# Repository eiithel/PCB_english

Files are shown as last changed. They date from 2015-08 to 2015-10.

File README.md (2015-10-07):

#**Introduction**  
There is currently no cure for autism. Special educators often struggle to communicate with children
sometimes immured in their silence. Autistic children can develop their language and facilitate their
interpersonal interactions with the help of early childhood management and special education.   
According to recent studies, the robot is a relevant tool for reducing some autistic symptoms, such as
joint attention deficit disorder. It also promotes generalization of skills.   
I proposed a new hardware and software architecture for Leka's first educational robot, as an extension
to its control system. This new architecture is based on a Linux kernel.   
This expansion provides support for experimentation and verification of embedded Linux applications
for a robotic base.    
**Key words**: robotics, autism, hardware conception, embedded linux

##**Functional requirements**

This card has been developed for the purpose of writing code at rapid speeds. It isn't the final version of Moti but it will be rather useful for developers, helping them to realize their tests and to validate this type of architecture. The card allows connection between `actuators` that permits the robot to live and to move and there are also `sensors` that permit the robot to be aware of its environment and to react consequential to that environment.

* Actuators
  * Motor control
  * RGB LEDs control
*  Datas/Sensoring
  *  Accelerometer/gyroscope
  *  Microphone

_the video is not supported in this version._

##**Components choice**

###Control part

* **Teensy 3.1**  



The control card is equipped with a __Teensy__ ARM Cortex 32 bits, a powerfull 32 bits MCU.   
This module is suitable for `C/C++` programming and is compatible with code written for __Arduino__. It is also featured with a large number of IO pinouts (_total of 34_). The Teensy is dedicated to three tasks :

*  Communicate to the __Arietta__ informations concerning the differents modules/sensors and to manage the different requests.
* To deploy 12 GPIO and one serial port.
* To Manage enslavement motor calculations.

>The code written on this card doesn't have to be modified. It should have just the simpliest code possible.
.

   * **Arietta**  
  

The __Arietta__ is a little embedded linux system based on a very swift ARM9. (_400MHZ_) it is equipped with a WIFI module, several GPIOs and a serial port connected to the __Teensy__. This comprises the central intelligence of the robot and is dedicated to several tasks :

  * To receive and to send information and requests to the __Teensy__.
  * To manage all Moti's intelligence. (_This part can be developped on a computer before being embedded on the card_).
  * Web server in order to develop applications permitting a certain number of clients to use its services (_Smartphones and tablets_).

>An Arietta's i2C bus is available on the card to add eventual sensor.   

A simple example of how to communicate beetween Arietta and Teensy :  
<https://github.com/eiithel/node_Serial>   
I used NodeJS for my tests.

###Motors

Motors are controlled by the control card but they need a dedicated integrated circuit to supply them enough power in order to run correctly. This is what permits the POLULU module based on a __TB6612FNG__ chip.

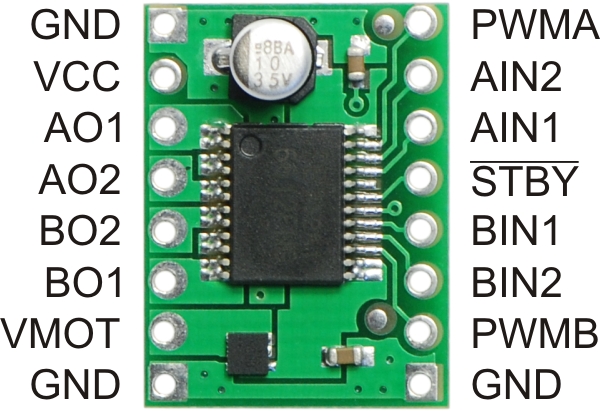
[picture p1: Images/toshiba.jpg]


PWMs and logic (AIN, BIN) are provided by the **Teensy**.

You can see a use case here: <https://github.com/eiithel/motors_test>    

>Be carefull. The **Teensy** is provided by 3 Timers.  
Motors PWMs come from **Timer0** but this timer is already used for **GSCLK** and **SIN** signals of the **TLC** due to pin sharing.  
You have to replace this PWMs by Outputs provided by Timer2 which is not used.  
This Timer is located under the **Teensy** (_pins 25 & 32_).

### **RGB LEDs**

In order to pilot 6 RGB LEDs, we need 6*3 = 18 channels. It is out of the question to use all the PWM Teensy outputs for that. The trick is to use a LED's driver that will allow us to increase our number of avalaible PWM outputs. This driver is controlled by the i2C Bus and provids 16 PWM channels. The 2 missing channels will be provided by the Teensy itself. The used component is the __TLC5940__ (Texas Instrument).



You can see a use case here: <https://github.com/eiithel/TLC4950_test>

##**Supplies**

The robot is designed with separate voltage regulators for digital and analog supply.   
The control part of the architecture needs to be supplied by 5V. The motor and its components need 6V. The solution was to use DC/DC adjustable regulators in order to provide good tensions scales.

**PTN78000WAH** _(Texas Instrument)_



This component can supply a max output current of 3A which is enough to run motors. It works for a 7 to 36V wide input tension. It permits to obtain a 2.5 to 22V wide output regulate tension. The output voltage is set using a single external resistor.

* 21 kohm for `5V`
* 13 kohm for `6V`
 
>All the passive components of the circuit are _SMD_ in order to save space on the board.

__BE CAREFULL__

This input is not protected against over and reverse voltages.  
When supplying the board take care to not invert anode and cathode. It would cause irreversible damages to the whole board.

###**A little display of the card**

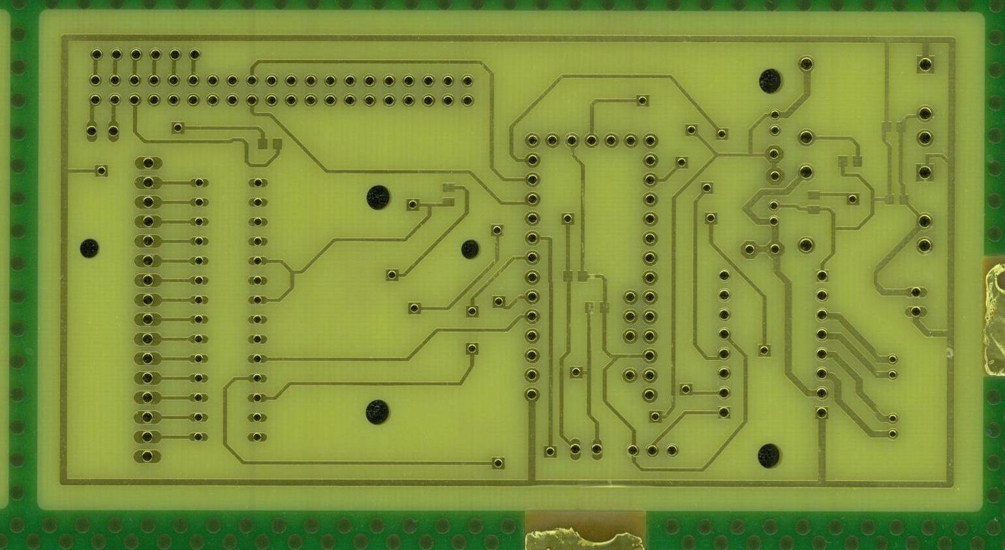
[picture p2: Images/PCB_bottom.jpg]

> <center>_Bottom face_</center>

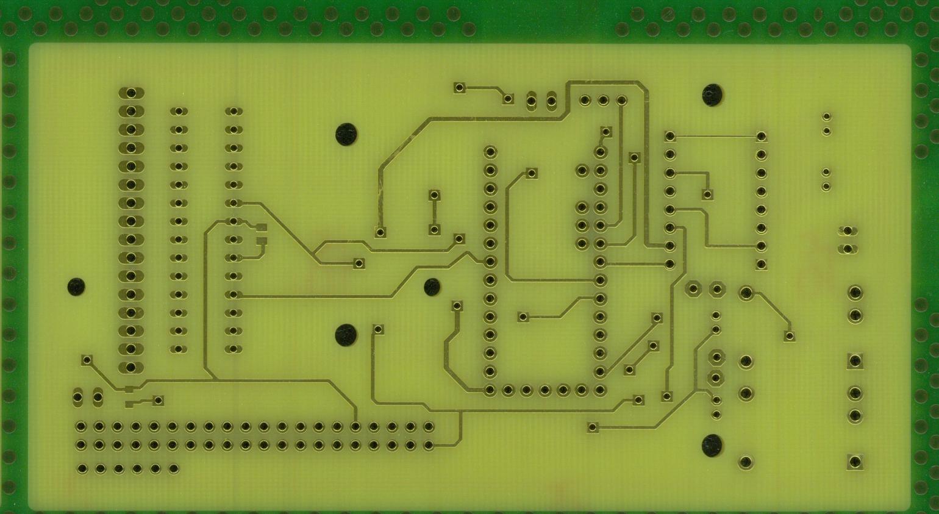
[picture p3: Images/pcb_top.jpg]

><center>_Top face_</center>

###__Bloc diagram__

To sum up, here is the electronical architecture of the prototype:

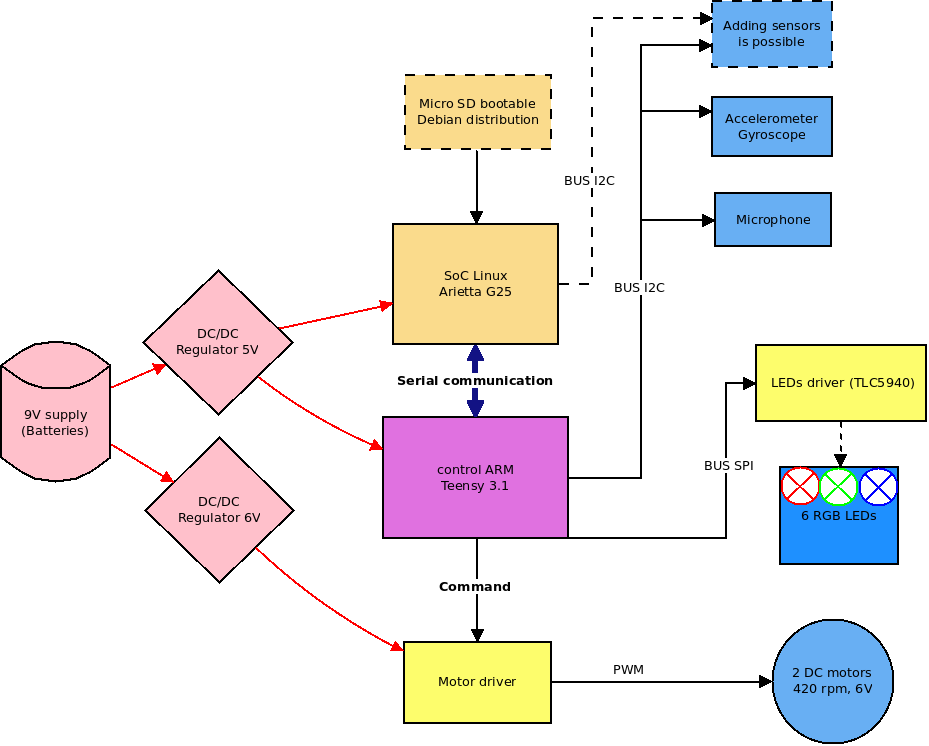
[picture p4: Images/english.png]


--
And the final view with some little errors to correct:   

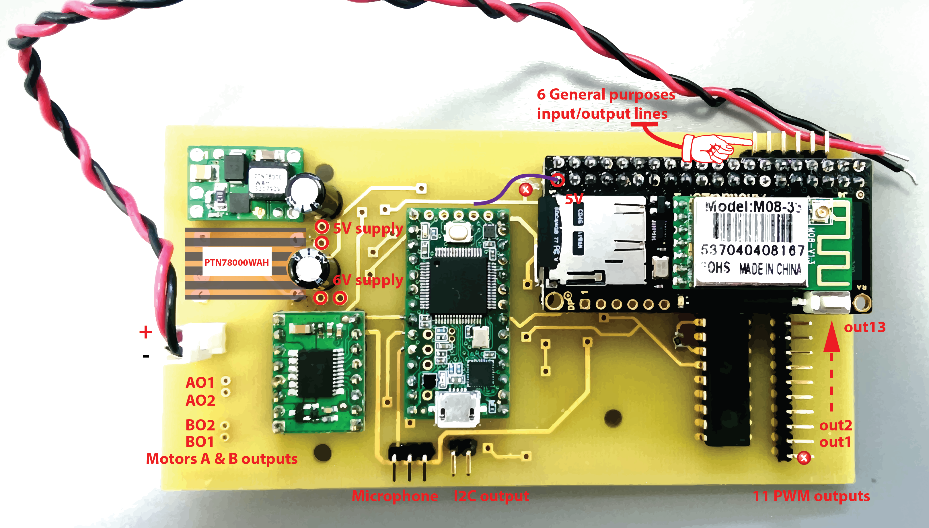
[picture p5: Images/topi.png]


<center>_Final view_</center>

> Written by Eiithel.

<a href="https://fr.linkedin.com/pub/ethel-marquer/84/151/485" style="text-decoration:none;"><span style="font: 80% Arial,sans-serif; color:#0783B6;">Voir le profil LinkedIn de Ethel Marquer&nbsp;Voir le profil de Ethel Marquer</span></a>

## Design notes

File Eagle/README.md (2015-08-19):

#Instructions

In the `lb` repertory you can find all the libraries used for the pcb design.

*   robot_insa_V1.lbr for __AriettaG25__
*   Teensy3.0.lbr for __Teensy__
*   TI-Eagle_library.lbr for __PTN78000WAH__
*   TLC5940.lbr for the __TLC__

Eagle files are located in the `Eagle` reportory.

* `leka.sch` is the schematic, this file represents the circuit diagram.
Parts are placed on many sheets and are connected together through ports.

* `leka.brd` represents the "_physical_" PCB. In this file, traces are connected 
besides the connections defined in the schematic.   
The auto-route function didn't 
have been used because the optimisation is worst with this method.  
Take the time to realize your own routes. Mountage will be easier!

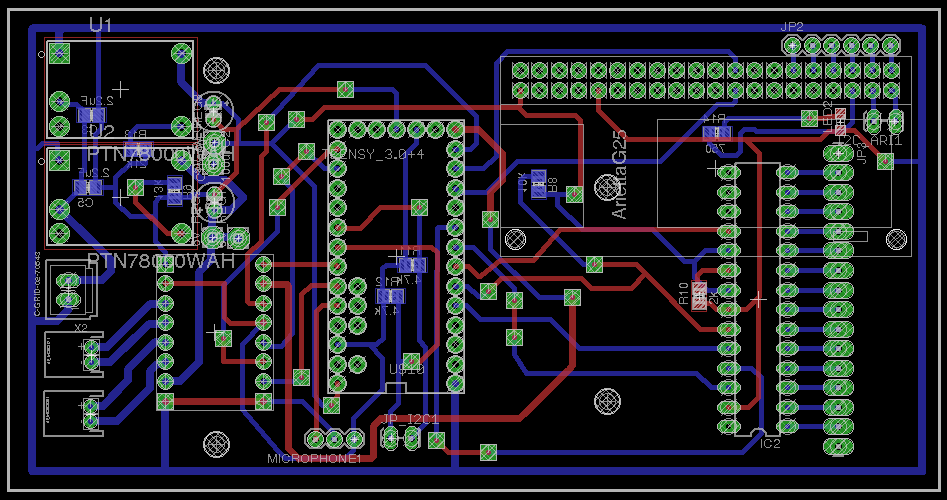
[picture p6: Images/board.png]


> A little display of .brd file

-----
-----

>If you order this PCB from a PCB manufacturer, **DON'T** ask for serigraphy.
Indeed, there is a lot of "stop mask" issues during DRC checking and this problem can be simply resolved by deleting this layer. 
The explanation is that Serigraphy layer prints onto top or bottom copper and that isn't correct.

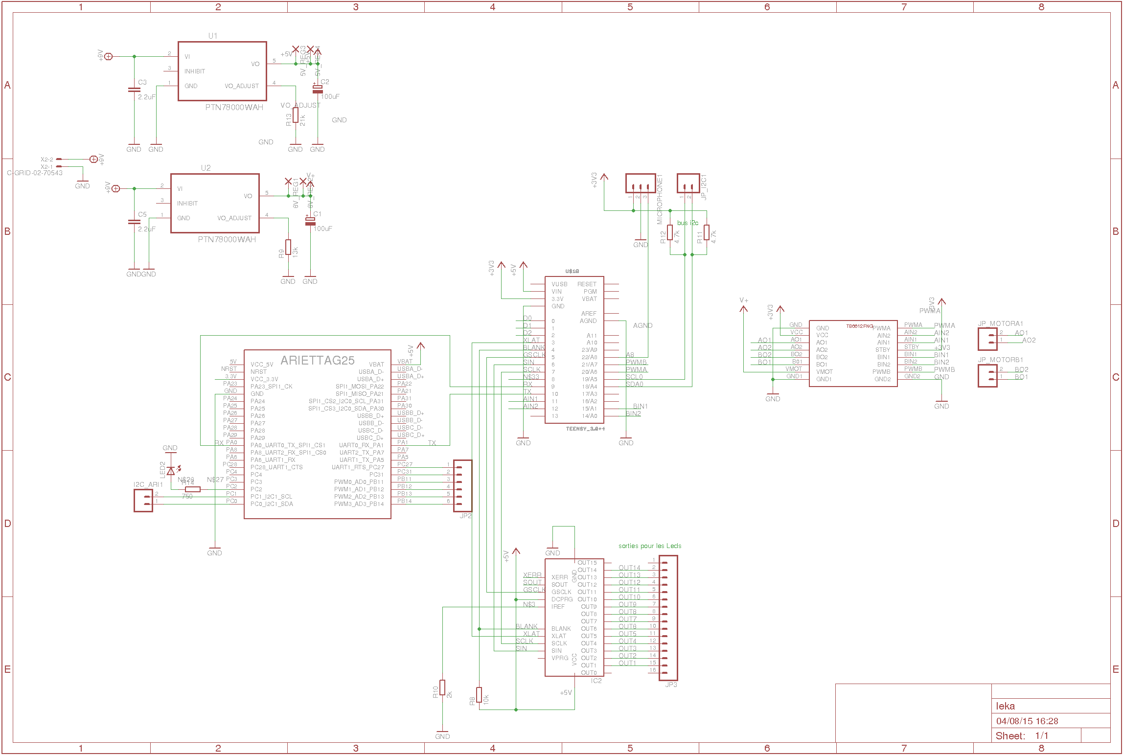
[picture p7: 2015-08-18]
Images/sch.png

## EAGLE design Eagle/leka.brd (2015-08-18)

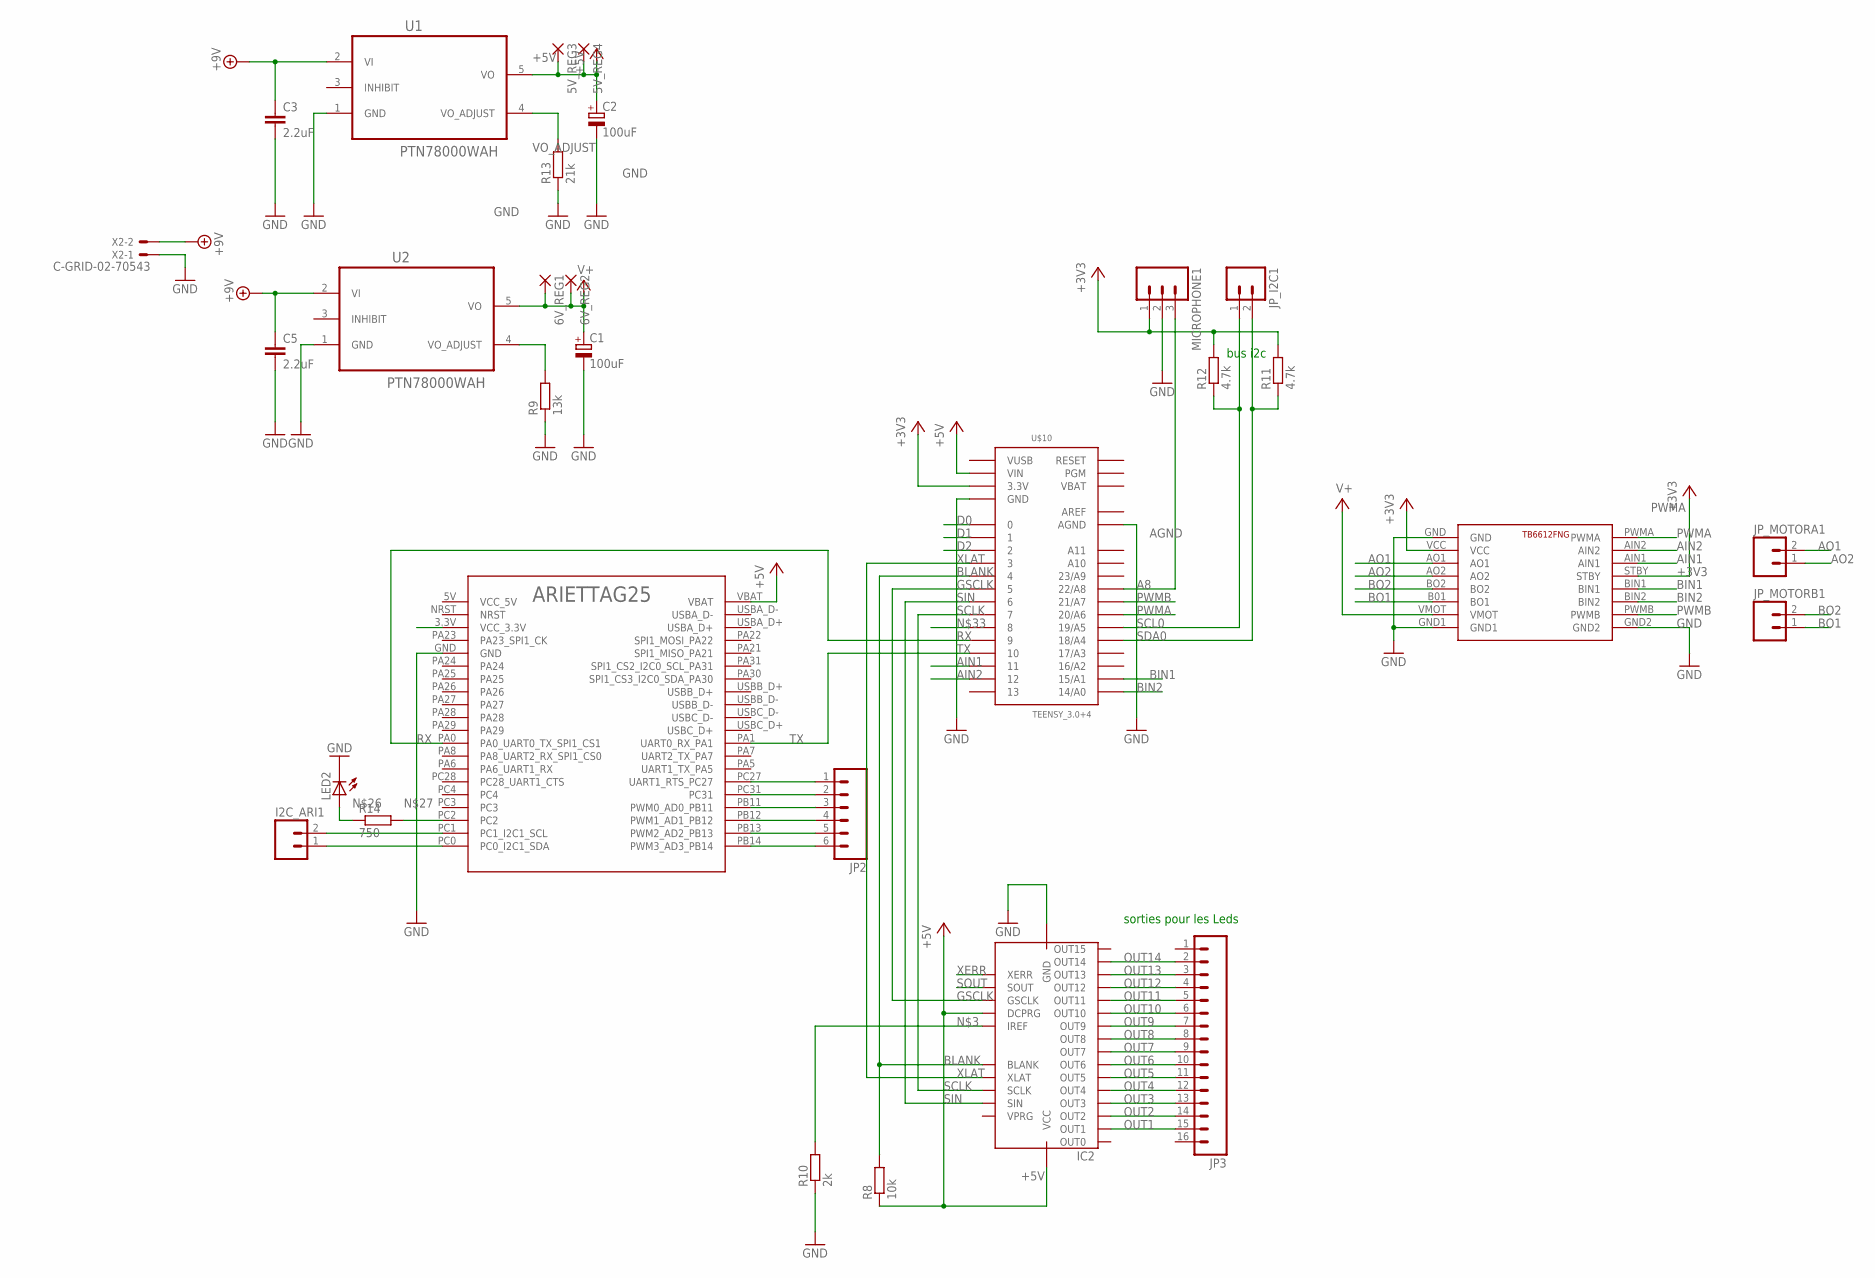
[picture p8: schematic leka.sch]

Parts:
5V_REG3, 5V_REG4, 6V_REG1, 6V_REG2: 2,54/0,9
C1, C2: 100uF; E2-5
C3, C5: 2.2uF; C0805
I2C_ARI1: M02LOCK_LONGPADS; 1X02_LOCK_LONGPADS
IC2: IC-PACKAGE_DIL28-3
JP2: M06SILK_FEMALE_PTH; 1X06
JP3: M16LONGPADS; 1X16_LONGPADS
JP_I2C1: M02LOCK_LONGPADS; 1X02_LOCK_LONGPADS
JP_MOTORA1: M02JST-PTH-2; JST-2-PTH
JP_MOTORB1: M02JST-PTH-2; JST-2-PTH
LED2: LEDSML0805; SML0805
MICROPHONE1: M03PTH; 1X03
R8: 10k; M0805
R9: 13k; M0805
R10: 2k; M0805
R11, R12: 4.7k; M0805
R13: 21k; M0805
R14: 750; M0805
U1, U2: PTN78000WAH; TI_PTN78000WAH
U$2: ARIETTAG25/256; ARIETTAG25
U$6: TB6612FNG; MOTOR_DRIVER
U$10: TEENSY_3.0+4
X2: C-GRID-02-70543; 70543-02

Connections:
+3V3: MICROPHONE1.1, R11.2, R12.2, U$6.STBY, U$6.VCC, U$10.3.3V, U$10.3.3V1 (3.3V)
+5V: 5V_REG3.1, 5V_REG4.1, C2.+, IC2.19 (DCPRG), IC2.21 (VCC), R8.1, U1.5 (VO), U$2.VBAT, U$10.VIN
+9V: C3.1, C5.1, U1.2 (VI), U2.2 (VI), X2.2
A8: MICROPHONE1.3, U$10.22/A8
AGND: U$10.AGND
AIN1: U$6.AIN1, U$10.11
AIN2: U$6.AIN2, U$10.12
AO1: JP_MOTORA1.2, U$6.AO1
AO2: JP_MOTORA1.1, U$6.AO2
AREF: U$10.AREF
BIN1: U$6.BIN1, U$10.15/A1
BIN2: U$6.BIN2, U$10.14/A0
BLANK: IC2.23 (BLANK), R8.2, U$10.4
BO1: JP_MOTORB1.1, U$6.B01 (BO1)
BO2: JP_MOTORB1.2, U$6.BO2
D0: U$10.0
D1: U$10.1
D2: U$10.2
GND: C1.-, C2.-, C3.2, C5.2, IC2.22 (GND), LED2.C, MICROPHONE1.2, R9.1, R10.1, R13.1, U1.1 (GND), U2.1 (GND), U$2.GND, U$6.GND, U$6.GND1, U$6.GND2, U$10.GND, U$10.GND1 (GND), X2.1
GSCLK: IC2.18 (GSCLK), U$10.5
unnamed: IC2.20 (IREF), R10.2
unnamed: I2C_ARI1.1, U$2.PC0 (PC0_I2C1_SDA)
unnamed: I2C_ARI1.2, U$2.PC1 (PC1_I2C1_SCL)
unnamed: R9.2, U2.4 (VO_ADJUST)
unnamed: JP2.6, U$2.PB14 (PWM3_AD3_PB14)
unnamed: JP2.5, U$2.PB13 (PWM2_AD2_PB13)
unnamed: JP2.4, U$2.PB12 (PWM1_AD1_PB12)
unnamed: JP2.2, U$2.PC31
unnamed: JP2.1, U$2.PC27 (UART1_RTS_PC27)
unnamed: JP2.3, U$2.PB11 (PWM0_AD0_PB11)
unnamed: LED2.A, R14.1
unnamed: R14.2, U$2.PC2
OUT1: IC2.1 (OUT1), JP3.15
OUT2: IC2.2 (OUT2), JP3.14
OUT3: IC2.3 (OUT3), JP3.13
OUT4: IC2.4 (OUT4), JP3.12
OUT5: IC2.5 (OUT5), JP3.11
OUT6: IC2.6 (OUT6), JP3.10
OUT7: IC2.7 (OUT7), JP3.9
OUT8: IC2.8 (OUT8), JP3.8
OUT9: IC2.9 (OUT9), JP3.7
OUT10: IC2.10 (OUT10), JP3.6
OUT11: IC2.11 (OUT11), JP3.5
OUT12: IC2.12 (OUT12), JP3.4
OUT13: IC2.13 (OUT13), JP3.3
OUT14: IC2.14 (OUT14), JP3.2
PWMA: U$6.PWMA, U$10.20/A6
PWMB: U$6.PWMB, U$10.21/A7
RX: U$2.PA0 (PA0_UART0_TX_SPI1_CS1), U$10.9
SCL0: JP_I2C1.1, R12.1, U$10.19/A5
SCLK: IC2.25 (SCLK), U$10.7
SDA0: JP_I2C1.2, R11.1, U$10.18/A4
SIN: IC2.26 (SIN), U$10.6
SOUT: IC2.17 (SOUT)
TX: U$2.PA1 (UART0_RX_PA1), U$10.10
V+: 6V_REG1.1, 6V_REG2.1, C1.+, U2.5 (VO), U$6.VMOT
VBAT: U$10.VBAT
VCC_5V: U$2.5V (VCC_5V)
VO_ADJUST: R13.2, U1.4 (VO_ADJUST)
VUSB: U$10.VUSB
XERR: IC2.16 (XERR)
XLAT: IC2.24 (XLAT), U$10.3

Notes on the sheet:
sorties pour les Leds
bus i2c

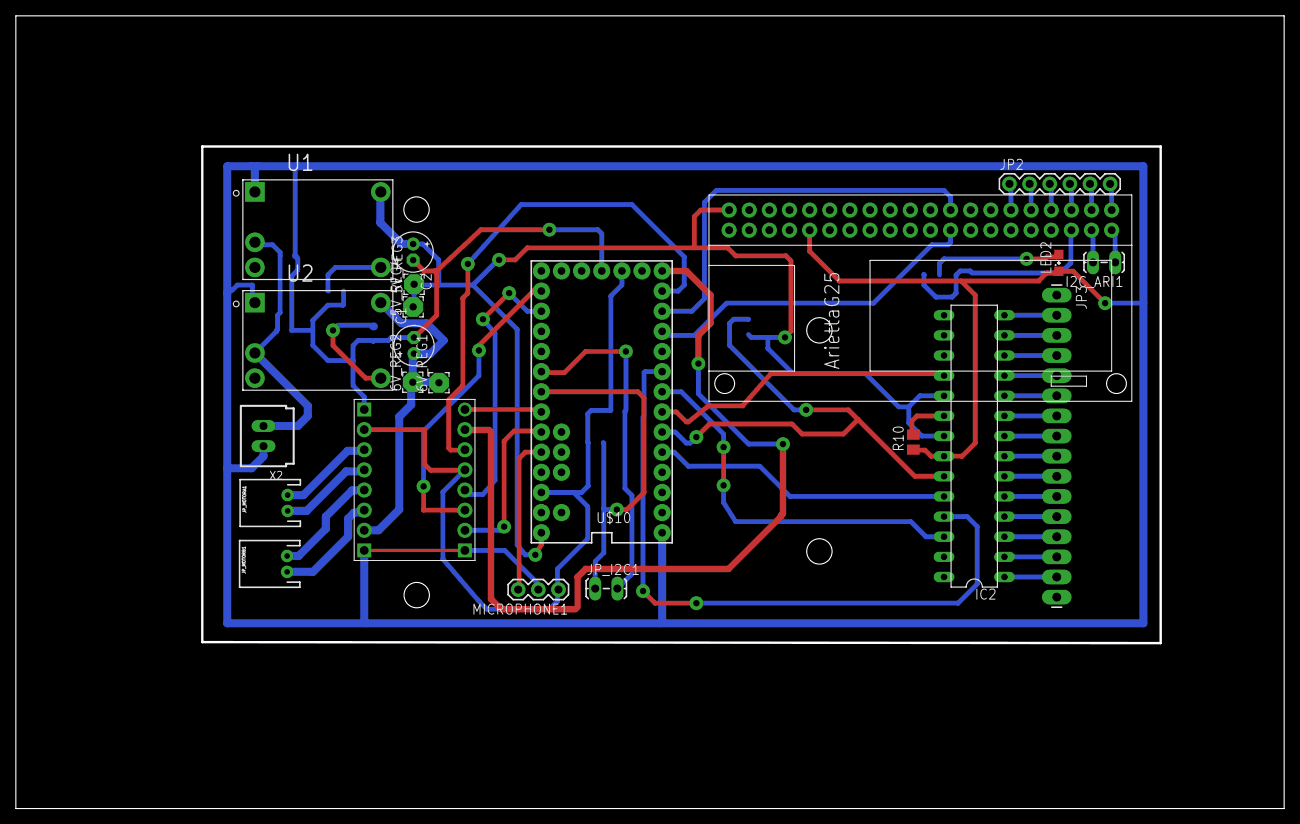
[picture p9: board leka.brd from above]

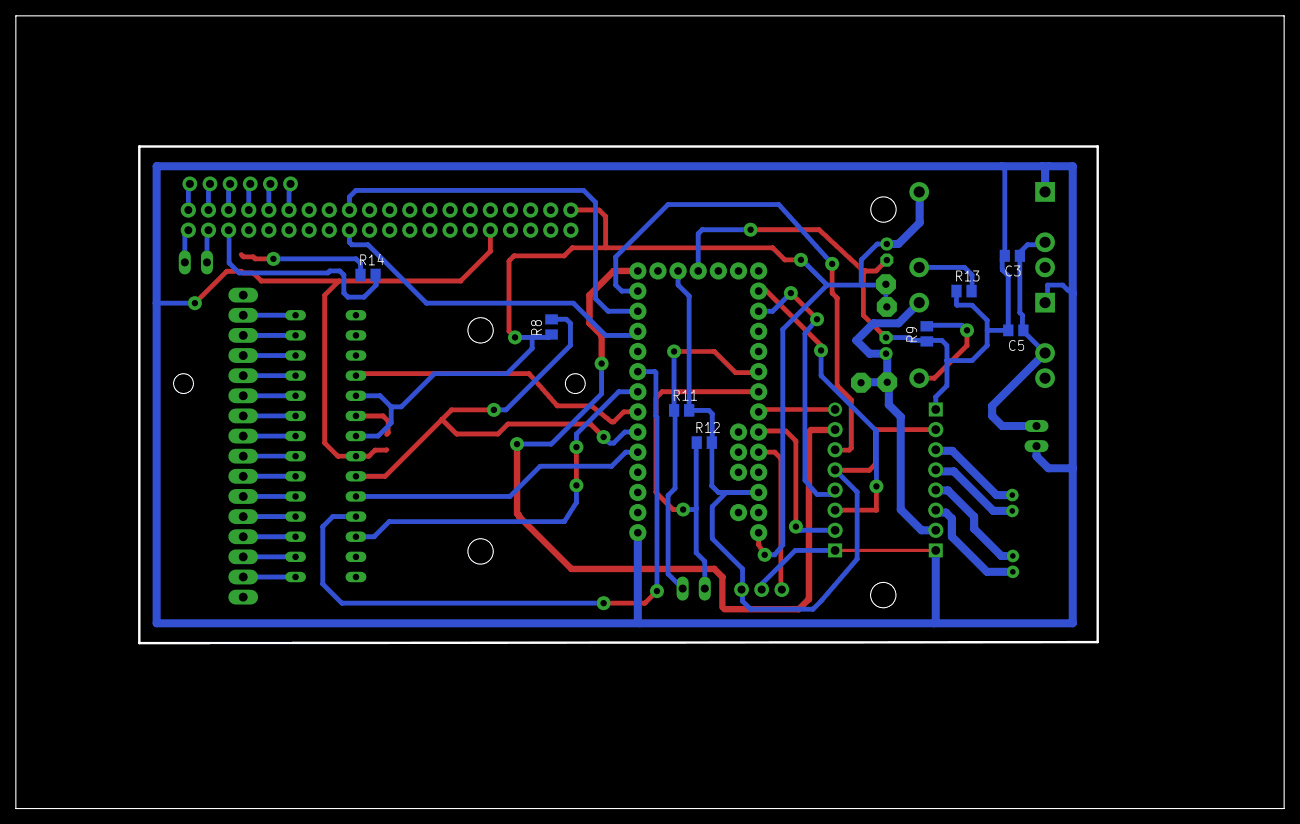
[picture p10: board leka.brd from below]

Board: 2 copper layers, 160.0 x 100.0 mm, 30 parts (8 on the bottom side), 52 nets.

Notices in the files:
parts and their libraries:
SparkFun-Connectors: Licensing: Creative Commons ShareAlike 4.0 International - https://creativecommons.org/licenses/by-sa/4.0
